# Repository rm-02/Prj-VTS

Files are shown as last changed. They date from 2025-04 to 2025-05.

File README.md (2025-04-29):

# Vibro-Tactile Stimulation Device Design Repository

This repository contains all of the hardware and software files required to manufacture a prototype device capable of delivering low-latency vibro-tactile stimulation.

The device uses Enhanced Shockburst to wirelessly trigger a vibration via a piezoelectric TDK powerhap 1313 haptic actuator. From button press on a peripheral NRF52 device to actuation on this receiving device takes ~1.3ms.

The device uses a magnetic battery connector to allow for easy to use hot swappable batteries. This reduces the time without the device or time required to be stationary. 

From full charge to dead the battery lasts ~9.5 hours when delivering 40ms of 100Hz vibration every 90ms.

Bare in mind that the device drives the piezo electric actuator at a high voltage, it is therefore imperative that it is handled safely. Please ensure the actuator leads are insulated from the skin, remove the battery before opening the device for any reason, and avoid water ingress into the case/actuator.

Below is an image of the assembled device, showing the dimensions when the battery is connected (in mm).



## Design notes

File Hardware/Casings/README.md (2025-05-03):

# Casing 3D Designs

This folder contains the required 3D models for the casings of the device.

## WARNING: 
Ensure the cables connected to the actuator are not in direct contact with the skin without insulation. This can cause significant EEG artefacts and even irritation when VTS is applied to certain areas of the body. The wires should be insulated and the terminals facing away from the skin, ideally further insulated with glue or some other method. Tape should be applied to the skin before the actuator is taped to ensure it is fully insulated and no sweat will reach the wires.

## Extra Information:
- All of the above was printed in PETG for the prototype

- 4 M2 screws and 2 M2 hex standoffs (6mm) were used to close the main casing

- Webbing of some kind is needed as a strap for the device to the upper arm, or a running armband for phones could possibly be used

- The charger casing has a small mounting postion for a magnetic connector, compatible with the battery packs. The charger used for the prototype was 	
Sparkfun's PRT-12711 as it was readily available, though any single cell li-po charger with max current of 800mA should work. Again, M2 screws and standoffs were used to close the casing.

- Some designs have a triangle fin attached for ease of 3D printing which can then be snapped off and filed till smooth.
  
- The main housing has wings to attach material for a strap which can then be buckled to the upper arm with the given buckle design (the buckle design is from https://www.printables.com/model/491473-camera-buckle).

- The actuator casing serves to increase pressure on the skin (making the vibrations feel stronger) and insulate it, though tape on the area of skin that it is placed may also be necessary to prevent sweat ingress and further insulate the actuator to avoid EEG artefacts. This can then be tightly taped to the skin with appropriate tape or held in place with a strap if using the mountable actuator sleeve. How well the tape has been applied (how taut it is with the skin)  seems to have an impact as to how strong the vibrations feel, this may take a few attempts to get used to.
  
- The battery leads should be cut and soldered to the corresponding magnetic connector terminals (view the PCB to see which pin is which, the flat sides were used on the PCB and charger whilst the pogo-pin sides was used on the batteries, there are 2 ground pins and one VDD, the battery used had a TH pin that was unused). The battery can then be slotted into the battery holder - the magnetic conncetor glued into the battery lid and the lid glued into the holder, creating a standalone battery pack. Note: the battery should be relatively loose in the holder when placing it in, li-po batteries may expand and this must be accounted for.

- The button can be placed into the recess in the wall of the main housing before the PCB is inserted, after which it will be held in place by the button.

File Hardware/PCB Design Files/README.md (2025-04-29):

# PCB Design Files

This Folder contains the PCB design files (board and schematic files) and gerber files for PCB ordering.

There is also a bill of materials from Mouser for all of the required components.

The battery used for the prototype was an 800mAh battery, chosen as the breadboard version had a peak current draw of ~650mA so a battery of at least 650mAh was required, assuming max discharge rate of 1C. The battery chosen is available at: https://cpc.farnell.com/unbranded/lp-573442-1s-3/battery-li-polymer-3-7v-800mah/dp/BT06808?st=bt06808

As mentioned in the root of the repo, the actuator chosen was powerhap TDK's 1313 actuator. To connect it to this design a JST-PH crimping set is also required.

The + symbols in the silkscreen next to the magnetic connector and JST connector denote the positive pins

The prototype board was assembled with a reflow oven, using solder paste with reflow temperature 235 degrees celsius. The magnetic connectors were then hand soldered after as they may melt in the oven



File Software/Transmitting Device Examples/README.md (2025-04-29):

This folder contains software examples for transmitting devices that would enable VTS.

USB_and_Button Example allows the NRF52 to be controlled by the provided Python app over USB to allow VTS waveform changes and sleep mode changes. It also triggers VTS when the voltage goes from low-high on pin D2 (P0.28), either by a connected button press or any other voltage trigger (0--> 3.3V). There is a debounce mechanism implemented to avoid the button press activating 2 VTS but this timeout has been set down to 50ms so should not pose an issue, if it does it can be set lower in src/main.c.

Time_Transmitter will simply make the NRF52 send a VTS enable packet over ESB every 90ms, useful for stress testing.

VTS triggers are sent by transmitting an ESB payload with the first byte {0x00}

VTS waveform changes are sent by transmitting an ESB payload with the first byte {0x01}

Sleep mode changes are sent by transmitting an ESB payload with the first byte {0x02}

To upload either program to the NRF52 devkit:

- Connect the devkit to your PC
- Double click the RST button on the devkit (next to the USB-C port) and a folder should appear on your PC
- Drag and drop the zephyr.uf2 file (from (Timed_Transmitter_Example or USB_and_Button_Example) --> build --> zephyr) from your PC to the folder
- Once complete, press the USER button again to reset the device, it should now be programmed and ready to be used

If you edit either file you can rebuild them in VSCode with Nordic Connect extensions. Set the bord to Nordic SOC/XIAO nrf52840 and add the device overlays. Use no sysbuild and then build the configuration

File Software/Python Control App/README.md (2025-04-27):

This Python application allows you to connect to an NRF52 development kit over USB and program it to send VTS waveform changes or sleep mode changes over ESB to the device.

It works with the USB_and_Button_Example given in Transmitting Device Examples

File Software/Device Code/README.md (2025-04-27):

The .zip file included here is the source code for the VTS device's microcontroller.

To upload this to the NRF52 devkit: 
- Connect the devkit to your PC
- Double click the RST button on the devkit (next to the USB-C port) and a folder should appear on your PC
- Drag and drop the zephyr.uf2 file (from VTS_Device_Code --> build --> zephyr) from your PC to the folder
- Once complete, press the USER button again to reset the device, it should now be programmed and ready to be used

The flow chart below shows how the program is set to behave from start up and on packet reception



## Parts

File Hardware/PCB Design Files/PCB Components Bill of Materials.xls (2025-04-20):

SHOPPING BASKET
This is not an invoice
20-Apr-25 14:54:52
 | Mouser No | Mfr. No | Manufacturer | Customer No | Description | RoHS | Lifecycle | Order Qty. | Price (GBP) | Ext.: (GBP)
1 | 915-BOS1921CQR | BOS1921CQR | Boreas Technologies |  | Motor/Motion/Ignition Controllers & Drivers Piezo haptic driver with digital front end in QFN | RoHS Compliant | New Product | 1 | £3.40 | £3.40
2 | 485-5360 | 5360 | Adafruit |  | Adafruit Accessories DIY Magnetic Connector - Right Angle Three Contact Pins | RoHS Compliant By Exemption |  | 2 | £4.86 | £9.72
3 | 810-CGA4J3X7R2E103K | CGA4J3X7R2E103K125AA | TDK |  | Multilayer Ceramic Capacitors MLCC - SMD/SMT CGA 0805 250V 0.01uF X7R 10% AEC-Q200 | RoHS Compliant |  | 1 | £0.123 | £0.12
4 | 810-C2012C0G2E392JAA | C2012C0G2E392J125AA | TDK |  | Multilayer Ceramic Capacitors MLCC - SMD/SMT 0805 250V 3900pF C0G 5% T: 1.25mm | RoHS Compliant |  | 1 | £0.212 | £0.21
5 | 963-TMK105BJ104KV8F | TMK105BJ104KV8F | TAIYO YUDEN |  | Multilayer Ceramic Capacitors MLCC - SMD/SMT 963-BAST105SB5104KF RPLCMT PN 25V 0.1uF X5R 0402 10% | RoHS Compliant |  | 4 | £0.082 | £0.33
6 | 80-T527I107M006ATE70 | T527I107M006ATE070 | KEMET |  | Tantalum Capacitors - Polymer 6.3V 100uF 1206 20% ESR=70mOhms | RoHS Compliant |  | 1 | £1.06 | £1.06
7 | 810-VLS3012HBX-100M | VLS3012HBX-100M | TDK |  | Power Inductors - SMD 3x3x1.2mm 10uH 20% Magnetic Pwr Inductr | RoHS Compliant |  | 1 | £0.401 | £0.40
8 | 603-AC0402JR-071K5L | AC0402JR-071K5L | YAGEO |  | Thick Film Resistors - SMD 1.5k Ohm 62.5mW 0402 5% AEC-Q200 Standard Power Version | RoHS Compliant By Exemption |  | 2 | £0.082 | £0.16
9 | 279-RLP73N1ER20FTDF | RLP73N1ER20FTDF | TE Connectivity |  | Current Sense Resistors - SMD RLP73N 1E R20 1% 1K RL | RoHS Compliant By Exemption |  | 1 | £0.319 | £0.32
10 | 485-1769 | 1769 | Adafruit |  | Adafruit Accessories JST-PH 2-pin SMT Right Angle Connect | RoHS Compliant |  | 1 | £0.613 | £0.61
11 | 942-IRLML6402TRPBF | IRLML6402TRPBF | Infineon |  | MOSFETs MOSFT P-Ch -3.7A 65mOhm 8nC Log Lvl | RoHS Compliant |  | 1 | £0.343 | £0.34
12 | 700-MAX16054AZTT | MAX16054AZT+T | Analog Devices Inc. |  | Supervisory Circuits On/Off Controller with Debounce and 15kV ESD Protection | RoHS Compliant |  | 1 | £2.82 | £2.82
13 | 710-436331045822 | 436331045822 | Wurth Elektronik |  | Tactile Switches Tact Switch SMT 1.65mm | RoHS Compliant |  | 1 | £0.474 | £0.47
14 | 652-CR0402FX-1002GLF | CR0402-FX-1002GLF | Bourns |  | Thick Film Resistors - SMD 10K OHM % | RoHS Compliant |  | 1 | £0.082 | £0.08
15 | 713-102010448 | 102010448 | Seeed Studio |  | Bluetooth Development Tools - 802.15.1 Seeed Studio XIAO nRF52840, MicroPython - Bluetooth 5.0 | RoHS Compliant |  | 1 | £8.82 | £8.82
By submitting your order you agree to these terms and conditions. (https://www.mouser.co.uk/saleterms) |  |  |  |  |  |  |  |  | Merchandise: | £28.86
Prices are reflected at the date and time shown. |  |  |  |  |  |  |  |  | Delivery Charge: | £12.00
 |  |  |  |  |  |  |  |  | Back-order Delivery: | £0.00

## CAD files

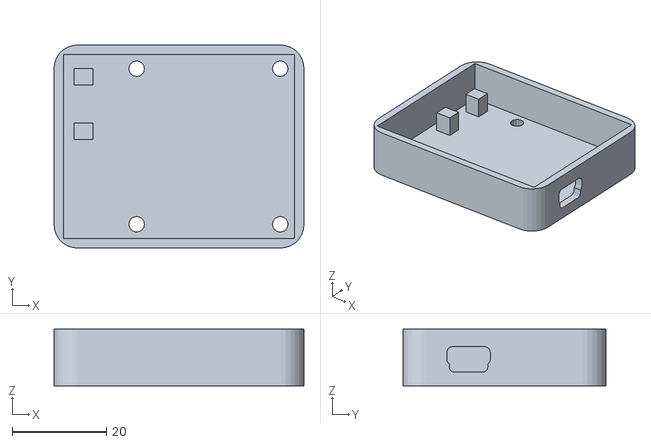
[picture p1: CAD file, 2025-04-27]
Hardware/Casings/Charger_Main_Casing.stl
53.1 x 43.1 x 12.0

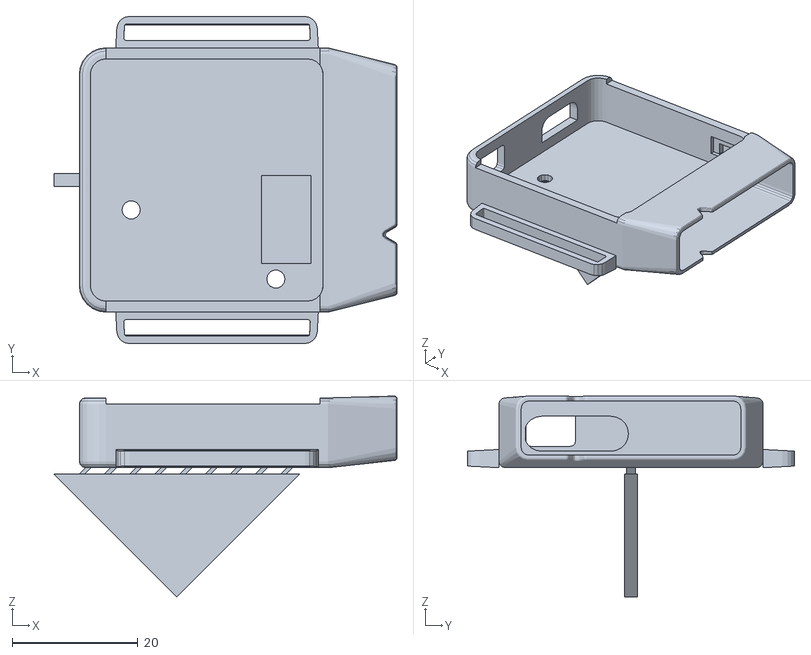
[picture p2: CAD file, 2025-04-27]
Hardware/Casings/Main_Casing.stl
54.5 x 52.0 x 31.9

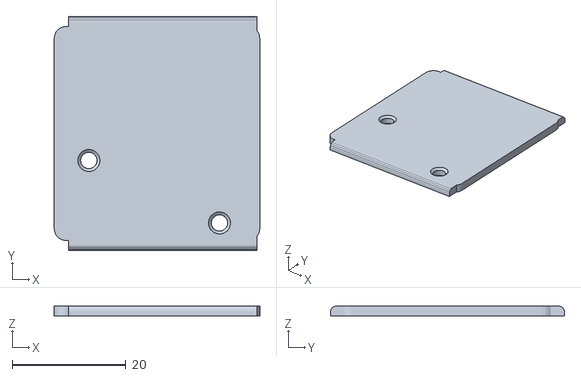
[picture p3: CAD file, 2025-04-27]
Hardware/Casings/Main_Casing_Top.stl
36.2 x 41.2 x 1.75

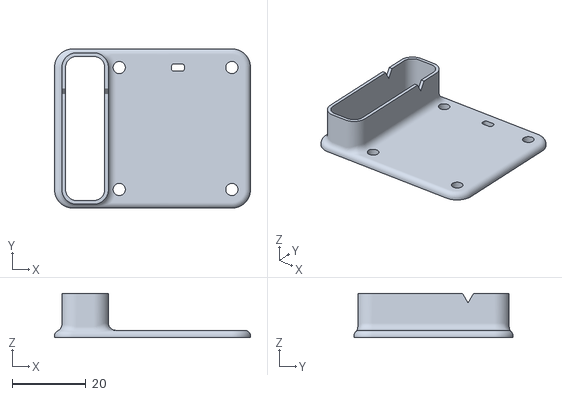
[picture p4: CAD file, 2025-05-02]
Hardware/Casings/Charger_Top.stl
53.1 x 43.1 x 12.0

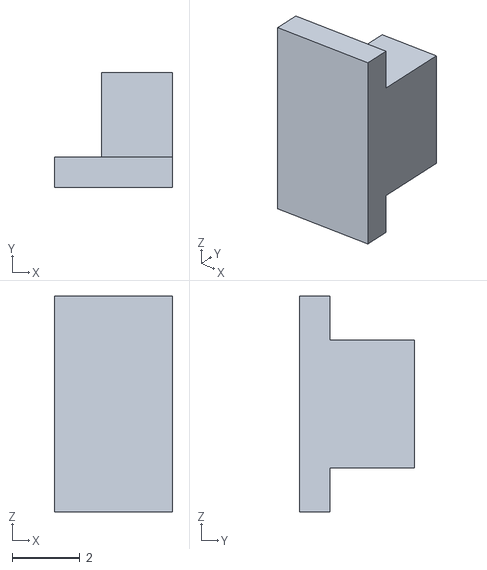
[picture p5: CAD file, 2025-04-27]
Hardware/Casings/Button.stl
3.50 x 3.40 x 6.40

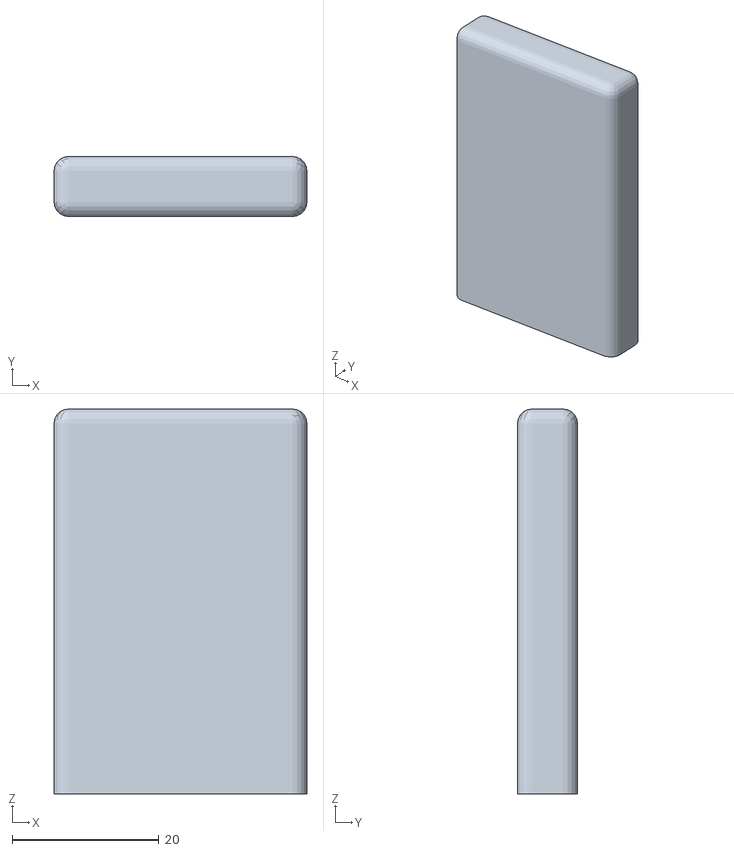
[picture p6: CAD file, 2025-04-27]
Hardware/Casings/Battery_Casing.stl
34.5 x 8.20 x 52.5

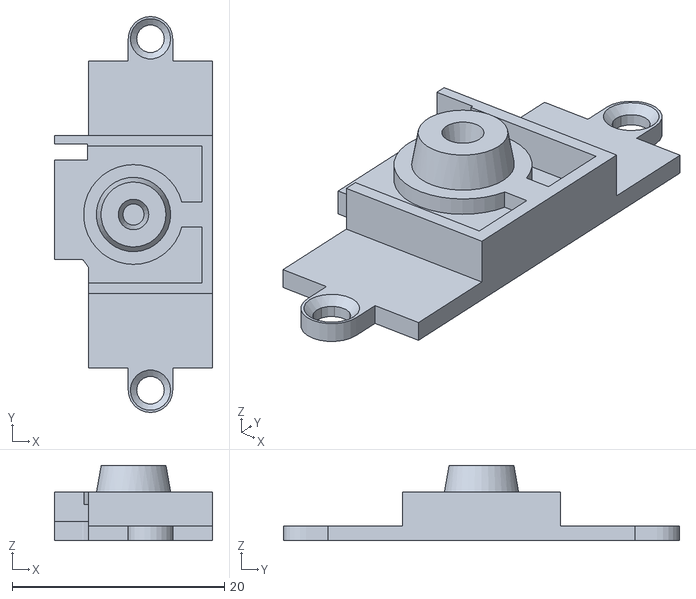
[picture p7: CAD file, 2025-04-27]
Hardware/Casings/Actuator_Sleeve_Mountable.stl
14.9 x 37.3 x 7.10

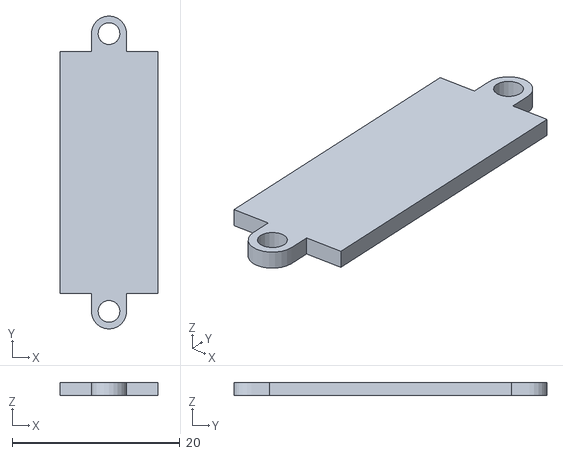
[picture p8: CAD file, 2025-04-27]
Hardware/Casings/Actuator_Sleeve_Mountable_Backplate.stl
11.7 x 37.3 x 1.60

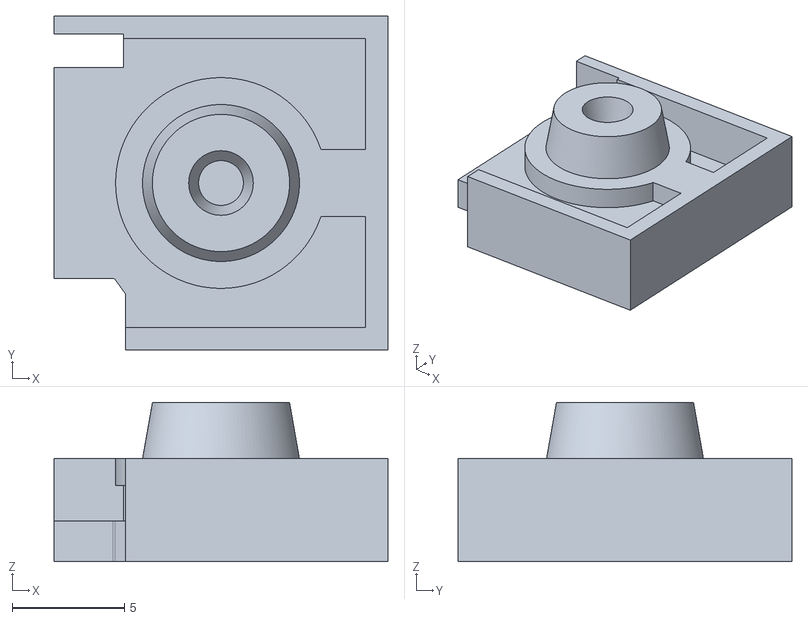
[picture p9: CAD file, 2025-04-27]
Hardware/Casings/Actuator_Sleeve.stl
14.9 x 14.9 x 7.10

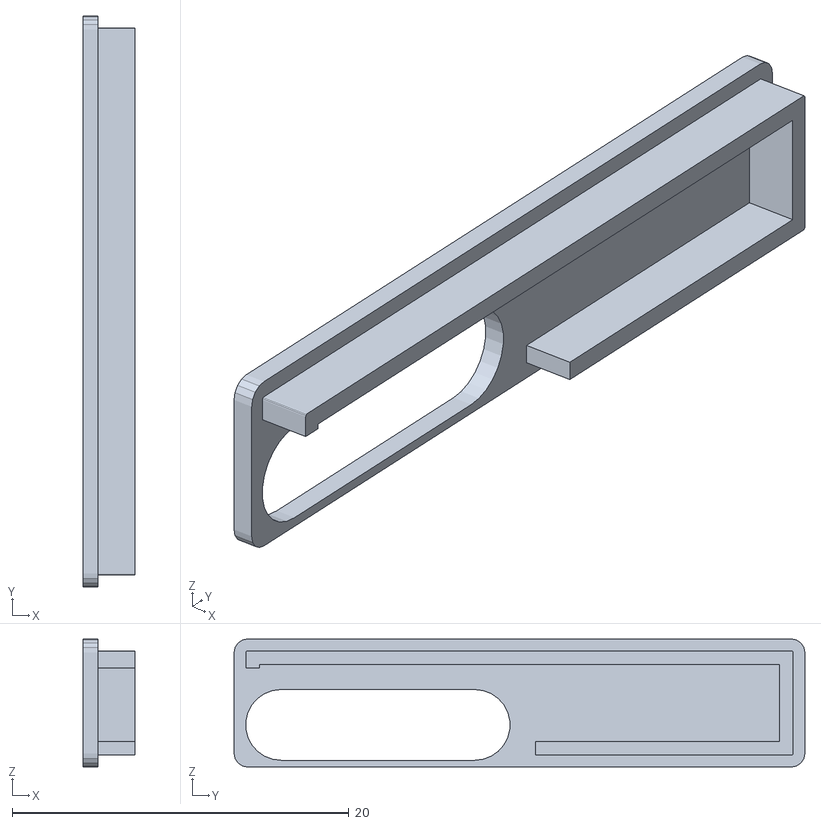
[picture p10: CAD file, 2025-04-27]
Hardware/Casings/Battery_Casing_Top.stl
3.10 x 33.9 x 7.60

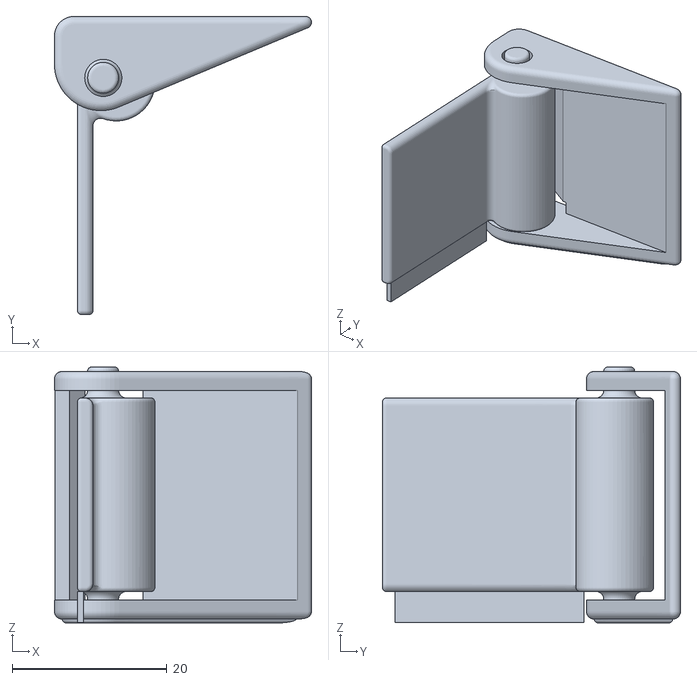
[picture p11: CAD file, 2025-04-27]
Hardware/Casings/Cam Buckle.stl
33.2 x 38.5 x 33.1
